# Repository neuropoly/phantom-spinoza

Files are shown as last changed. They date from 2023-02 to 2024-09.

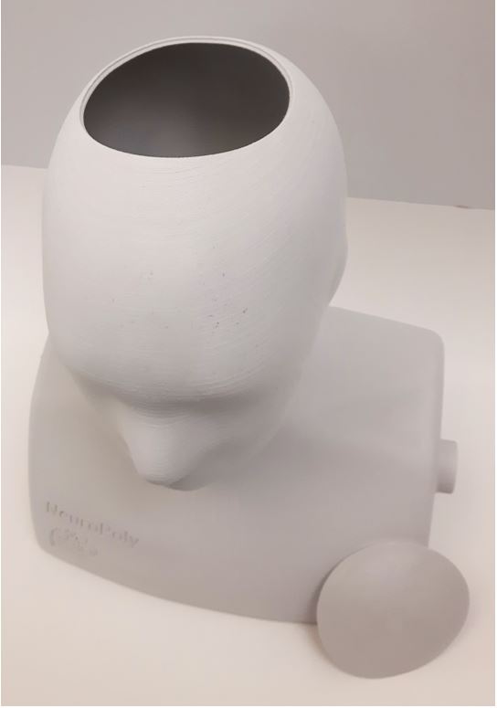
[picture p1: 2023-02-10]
Pictures/Assembly_1.JPG

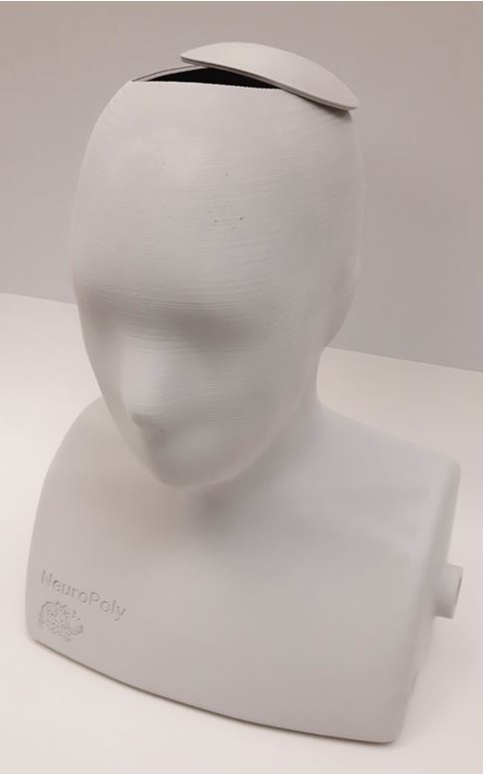
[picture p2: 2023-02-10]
Pictures/Assembly_2.JPG

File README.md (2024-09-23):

# phantom-spinoza



CAD model and recipe for MRI head-torso phantom fabrication



## Citation

> Lopez-Rios N, Gilbert KM, Papp D, Cereza G, Foias A, Rangaprakash D, May MW, Guerin B, Wald LL, Keil B, Stockmann JP, Barry RL, Cohen-Adad J. _An 8-channel Tx dipole and 20-channel Rx loop coil array for MRI of the cervical spinal cord at 7 Tesla_. NMR Biomed, 36(11):e5002, 2023. https://pubmed.ncbi.nlm.nih.gov/37439129/

## Recipe

Phantom physical characteristics:
- Inner volume: 14.156 L
- Total phantom weight: 16.257 kg

Ingredients:
- Water (demineralized): 9,900 mL
- Mouthwash (no alcohol): 600 mL (~4% of final volume)
- Salt: 254 g
- Sugar: 7,913 g
- Agar: 116g (0.75% of final volume)

<details><summary>Details about the ingredients</summary>

The recipe was based on [this website](https://amri.ninds.nih.gov/cgi-bin/phantomrecipe): 




> **Note**
> The mouthwash amount (600 mL) is included in the estimated water volume (10,500ml). Mouthwash is used to prevent the growth of bacteria that is likely to occur in a mixture containing sugar and agar. It was assumed that the efficacy of an alcohol-based mouthwash would be reduced due to the rapid evaporation of the alcohol portion during the mixing process due to the high temperature required. For this reason, an alcohol-free mouthwash was selected. 



</details>

## Parameters (@3T)

- Conductivity: 0.74 S/m
- Permittivity: 65.8
- T1: ~500 ms
- T2: ~50 ms
- T2*: ~10 ms

## Parameters (@7T)

- Conductivity: 0.78 S/m
- Permittivity: 63.3

> **Note**
> Our goal was to obtain a mixture that mimicked the average human tissue in the region of interest in terms of dielectric parameters and relaxation times. To do this, we had to find a trade-off between [sugar](https://aapm.onlinelibrary.wiley.com/doi/abs/10.1118/1.4895823) and [agar](https://aapm.onlinelibrary.wiley.com/doi/full/10.1118/1.3656077) concentrations, since both affect relaxation times, and sugar is used to control permittivity. This allowed us to keep the permittivity and relaxation times within the range of human tissues while still producing a gel.

## Tips

Phantom shell construction:
- Description: The phantom shell was divided in two parts for 3D printing to provide a hole of 110mm in diameter at the top of the head. This opening is needed to manually remove 3D-printed supports and finish the inner surface by sanding and waterproofing. The shell has also a D-shaped filling hole on one side where a PVC reducing bushing (Schedule 40 ¾ spigot X ½ FTP) is manually D-shaped and glued. After filling the phantom, the bushing is closed with a PVC plug (Schedule 40 ½ MPT).
- Printing material: PLA 2.0 EcoTough™
- Printer: Modix BIG-60
- Printing parameters: [NeckPhantom6](https://github.com/neuropoly/phantom-spinoza/blob/main/NeckPhantom6.curaprofile). 
- Remove all 3D-printing supports and residues from all surfaces.
- Smooth all surfaces carefully with sandpaper (120 and 220 grit).
- Waterproof inner surfaces by coating it with epoxy (e.g., Smooth-On, XTC-3D™). 
- After the inner surfaces of both parts are completely coated and dry, assemble the shell: glue or (plastic) weld its two sections and glue the PVC bushing. Use epoxy for gluing (J-B WELD, High Strength Plastic Bonder, Adhesive Syringe - Tan, 25 ml).
- Reinforce exterior surfaces with epoxy (e.g., Smooth-On, XTC-3D™) and fiberglass (#120-38 Standard E-Glass Fiberglass Cloth). The fiberglass provides the phantom with additional resistance to moderate impacts. This [video](https://www.youtube.com/watch?v=ioj1YBm6bJY) shows how to select the fiberglass and [this one](https://www.youtube.com/watch?v=ujk-wBQDUSk) describes how to apply it. 
- The fiberglass chosen is flexible, easy to work with, inexpensive, and strong enough for this application. Note that the Phantom is heavy when fully loaded (17kg) and a strong impact such as a drop will likely render the shell useless, even if a stronger and more expensive reinforcing material such as carbon fiber is used.
- Thoroughly clean the interior of the coated shell and test it for waterproofness by filling it with water and inspecting it after 24 hours.

Mixture preparation:
- Ensure that no contaminating particles can fall into the mixture.
- Place large container (20 liters) on a [hot plate](https://www.hubert.ca/product/75300/Cadco-CSR-3T-Stainless-Steel-Single-Burner-Hot-Plate-With-8Dia-Element---12-14L-x-14W-x-4-18W) and add water. A [hot pot with a faucet](https://www.homedepot.ca/product/camp-chef-19l-20-qt-aluminum-hot-water-pot/1001156780) is recommended.
- Turn the hot plate on and wait for temperature to reach 60deg.
- Start stirring and do not stop during the whole process. Avoid splashing. 
- Add salt and dissolve it.
- Add sugar gradually, dissolving each portion.
- Add agar when the temperature has reached 90 deg and dissolve it.
- Turn hot plate off. Continue stirring. 
- Add mouthwash and stir for a few minutes to homogenize the mixture. 
- Continue stirring for some time to prevent the mixture from burning at the bottom of the container.
- Wait for temp to reach 60 deg to to facilitate the release of air bubbles.
- Pour the mixture into the phantom avoiding bubbles. To do this, a hose connected to the pot's faucet and passing through the phantom inlet can be used to drive the mixture flow directly to one of the inner surfaces of the shell, as is done to fill a glass of beer.

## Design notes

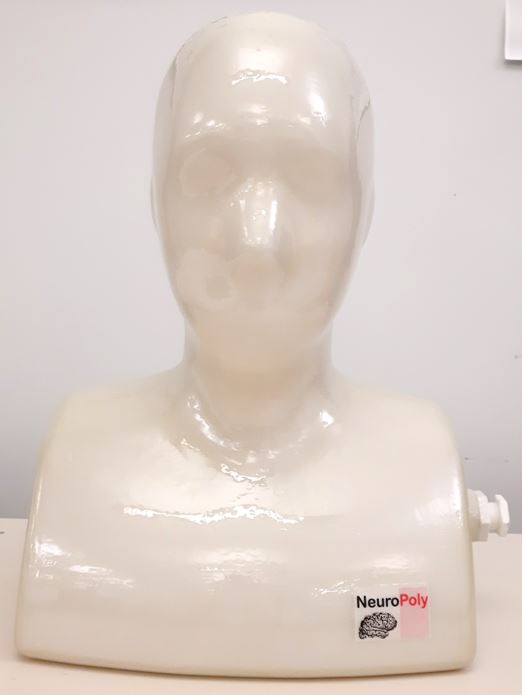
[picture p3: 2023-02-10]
Pictures/Front_view.JPG

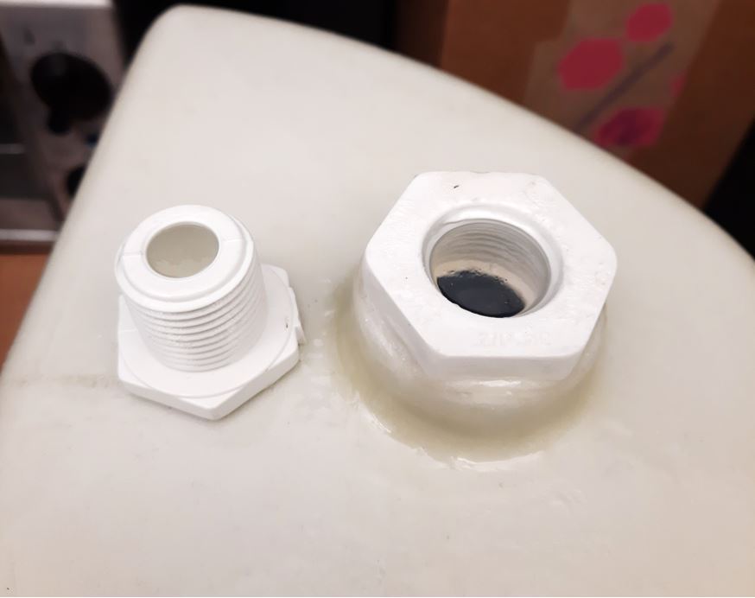
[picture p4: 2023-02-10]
Pictures/Filling_orifice_and_cap.JPG

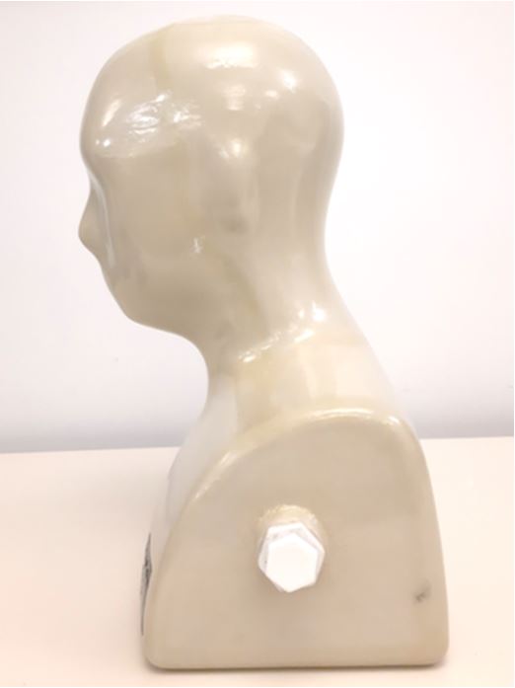
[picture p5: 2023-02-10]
Pictures/Side_view.JPG

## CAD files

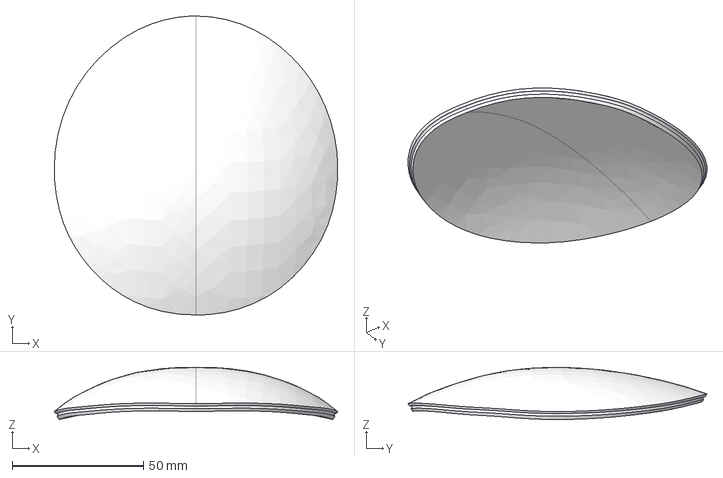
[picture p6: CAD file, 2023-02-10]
CAD_design/phantom_cap.igs
108.0 x 113.9 x 19.8 mm

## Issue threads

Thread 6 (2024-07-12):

### ISSUE TITLE
What recipe for v2

### ISSUE THREAD

**Issue by CharlesPageot** [neuropoly/phantom-spinoza#6]
For a project with shimming @4rnaudB would need to know the T1 of Spinoza v2 that is at UNF. @NLopezRios would you have the recipe for that version by any chance?

**Comment by NLopezRios** [comment]
Dielectric parameters @300MHz:

- Conductivity: 0.6 S/m
- Permittivity: 35.46

Recipe:

- Solvent: 960ml demineralized water + 40ml mouthwash
- Sugar: 1970g
- Salt: 253g
- Gadolinium: 1ml

**Comment by 4rnaudB** [comment]
Thank you!

**Comment by 4rnaudB** [comment]
> Dielectric parameters @300MHz:
> 
> * Conductivity: 0.6 S/m
> * Permittivity: 35.46
> 
> Recipe:
> 
> * Solvent: 960ml demineralized water + 40ml mouthwash
> * Sugar: 1970g
> * Salt: 253g
> * Gadolinium: 1ml
